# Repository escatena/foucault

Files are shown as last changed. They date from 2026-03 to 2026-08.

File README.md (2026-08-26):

# 📺 Watch the video

Watch on YouTube (https://www.youtube.com/watch?v=r8lBbuhs2y4)
Watch on YouTube (https://www.youtube.com/watch?v=cCXCGMFah08)

---

# 📌 Abstract
**A short driven Foucault pendulum at 26.9°S latitude**

In this paper it is discussed the construction of a short Foucault pendulum (2.4 meters long, compared to the several dozen meters typically found in museums and science centers). The pendulum is driven by a standard electromagnet and suspended using a small pin vise. A magnetic sensor is placed directly beneath the pendulum’s equilibrium point to track its motion, enabled by a small neodymium magnet attached to the bottom of the bob. The sensor is connected to an Arduino UNO board (ATmega328P), which processes the readings to control the electromagnet that provides controlled impulses to the pendulum, while also tracking the precession angle of the pendulum’s oscillation plane. This method eliminates the need for a secondary detection coil, commonly employed in similar setups, thereby simplifying the electronic circuit compared with other implementations. Using this approach, it was found a precession rate of 6.8 ± 0.3 °/h, in agreement with the expected theoretical prediction for our latitude.

The full paper describing the experiment can be fount at https://www.scielo.br/j/rbef/a/hsv8dhmVLGM85JyyM8W3H9k/?lang=en&ilang=pt_BR

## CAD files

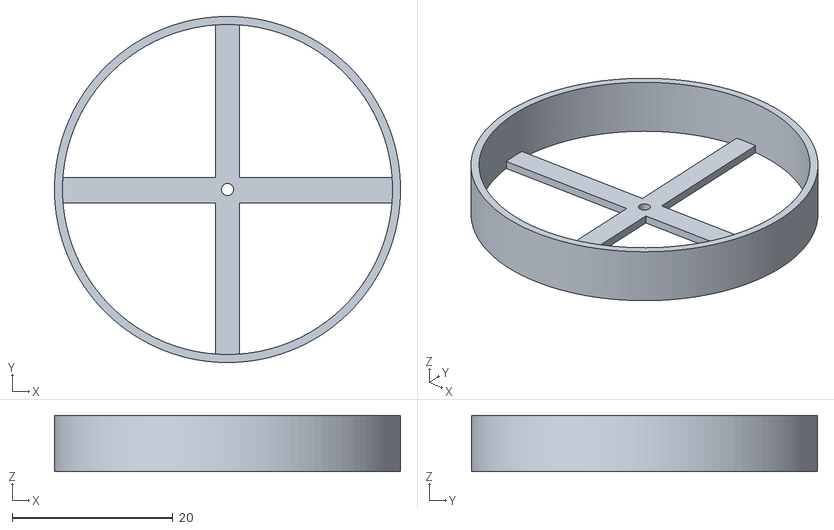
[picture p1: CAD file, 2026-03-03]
3D printed parts/Aligment tool/target.stl
43.0 x 43.0 x 7.00

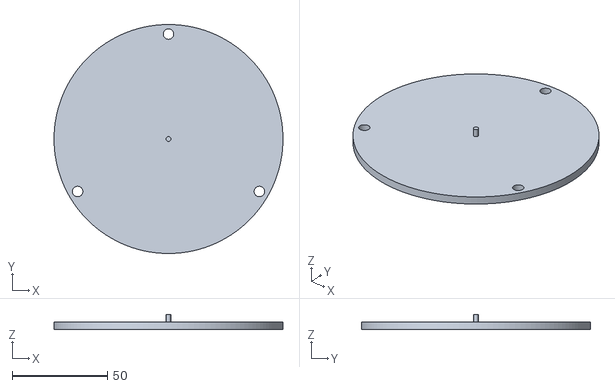
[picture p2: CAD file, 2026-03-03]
3D printed parts/Base/sensor support.stl
120.0 x 120.0 x 8.00

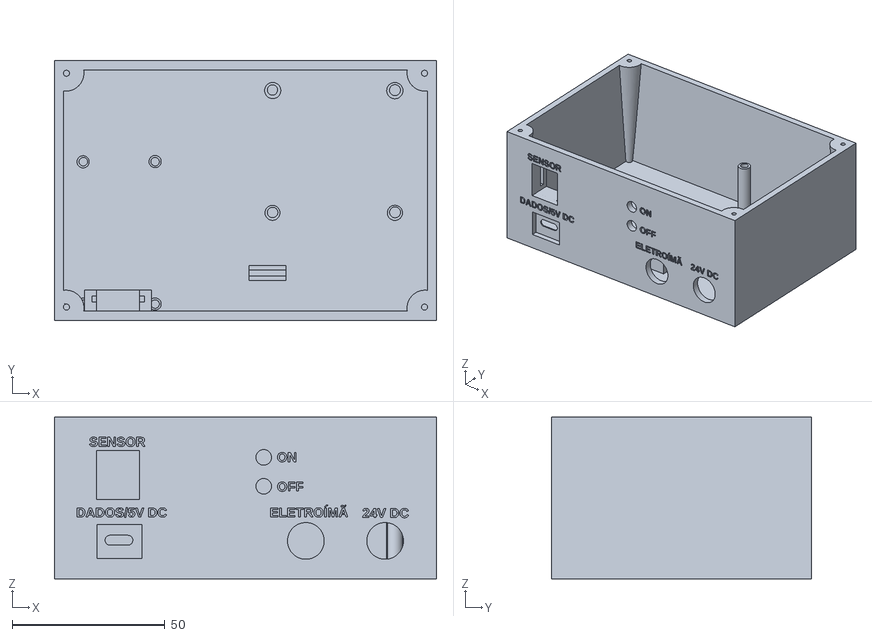
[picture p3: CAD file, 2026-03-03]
3D printed parts/Case eletronics/case-esp32.stl
125.0 x 85.0 x 53.0

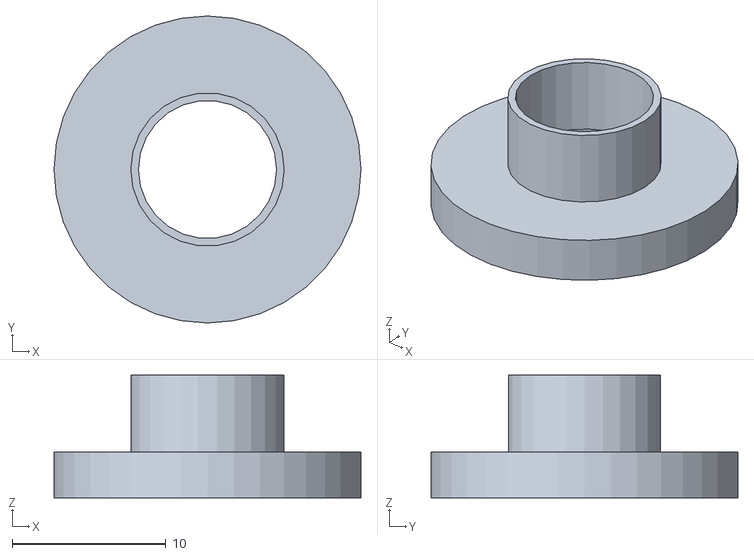
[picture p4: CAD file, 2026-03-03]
3D printed parts/Charron adapter/adaptador-charon-09.stl
20.0 x 20.0 x 8.00

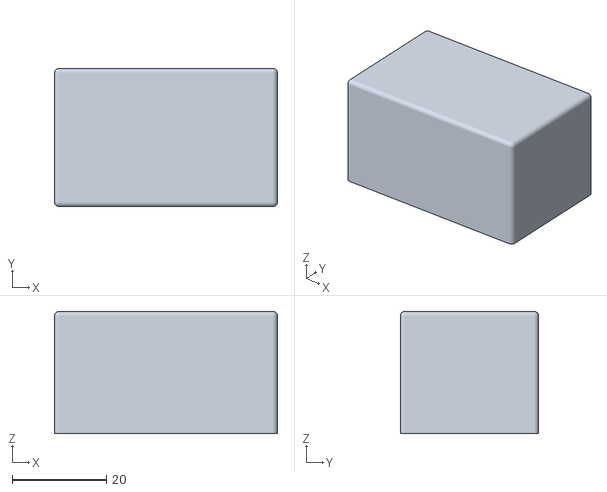
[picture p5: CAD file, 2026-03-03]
3D printed parts/Sensor case/case-sensor-lid.stl
47.4 x 29.4 x 26.0

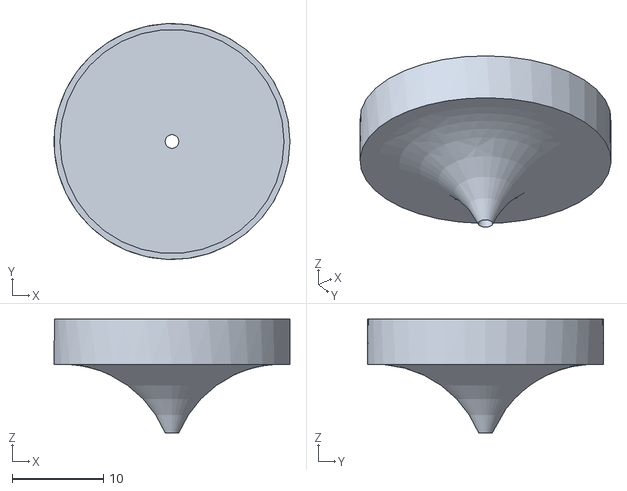
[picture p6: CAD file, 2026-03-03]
3D printed parts/Aligment tool/pointer.stl
25.9 x 25.9 x 12.5

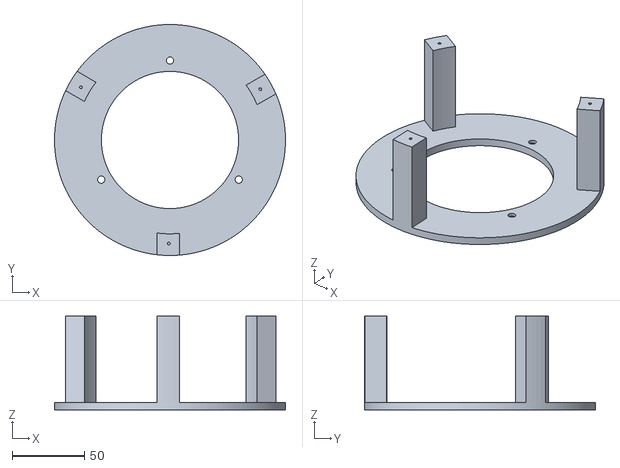
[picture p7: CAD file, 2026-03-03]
3D printed parts/Base/base.stl
160.0 x 160.0 x 65.0

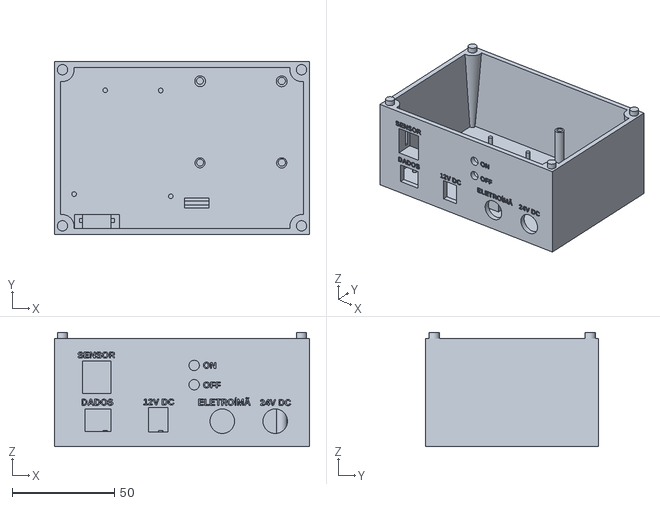
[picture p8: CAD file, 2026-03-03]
3D printed parts/Case eletronics/case-arduino.stl
125.0 x 85.0 x 56.0

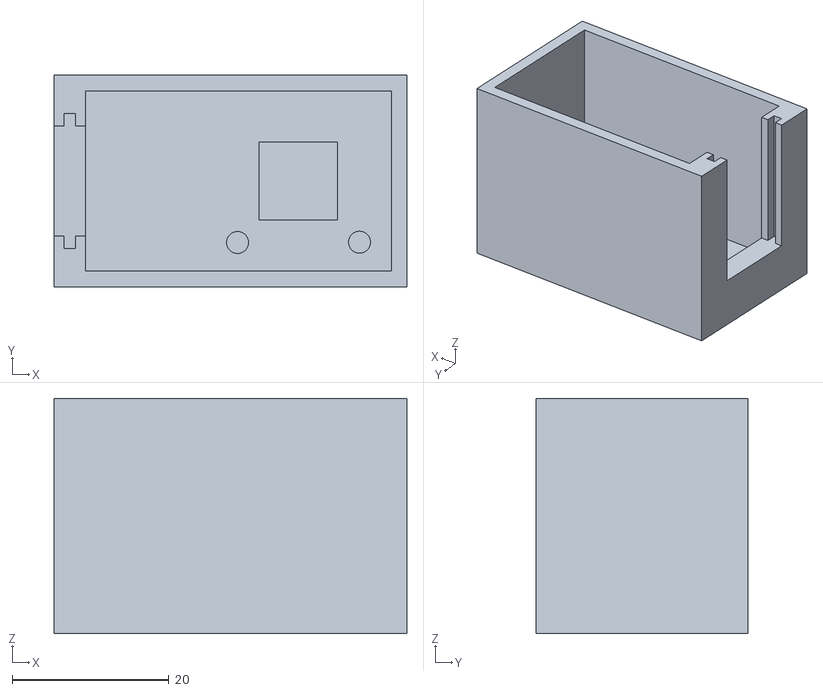
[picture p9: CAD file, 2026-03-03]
3D printed parts/Sensor case/case-sensor.stl
45.0 x 27.0 x 30.0

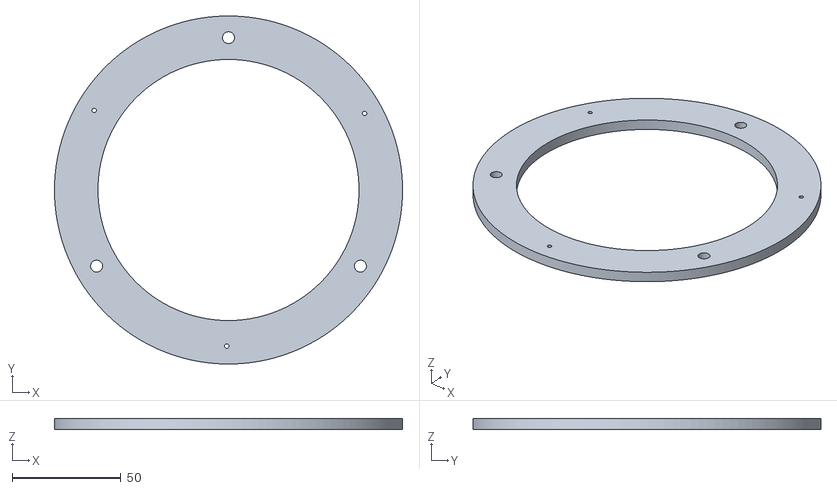
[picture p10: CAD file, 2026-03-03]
3D printed parts/Base/platform.stl
160.0 x 160.0 x 5.00

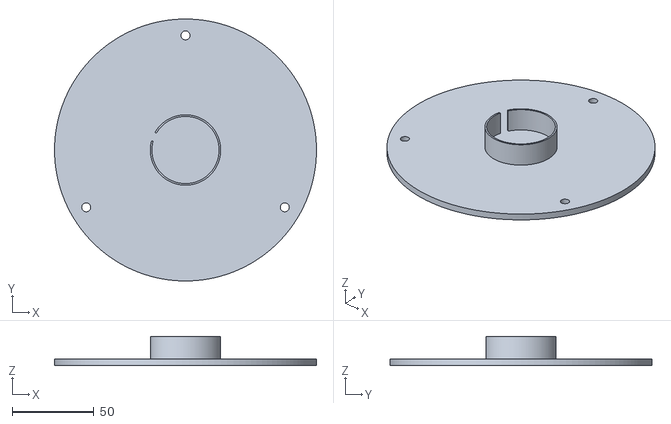
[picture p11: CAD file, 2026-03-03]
3D printed parts/Base/electromagnet support.stl
160.0 x 160.0 x 18.0

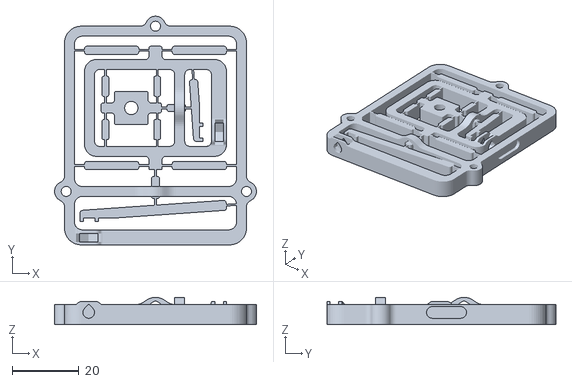
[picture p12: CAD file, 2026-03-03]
3D printed parts/Base/compliant mechanism.stl
60.5 x 68.5 x 8.22

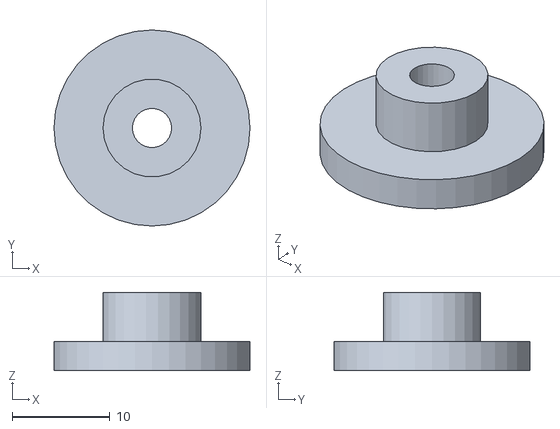
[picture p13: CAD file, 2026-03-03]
3D printed parts/Charron adapter/adaptador-charon-04.stl
20.0 x 20.0 x 8.00

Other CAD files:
3D printed parts/Charron adapter/adaptador-charon-07.stl
3D printed parts/Charron adapter/adaptador-charon-05.stl
3D printed parts/Charron adapter/center-charon.stl
3D printed parts/Charron adapter/adaptador-charon-06.stl
3D printed parts/Charron adapter/adaptador-charon-08.stl

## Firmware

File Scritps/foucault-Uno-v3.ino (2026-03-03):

#include <QMC5883LCompass.h>
#include <math.h>

QMC5883LCompass compass;

// =====================================================
// ================= PINS ==============================
// =====================================================

#define RIGHT_PWM 5
#define LEFT_PWM 4
#define RIGHT_ENABLE 3
#define LEFT_ENABLE 2
#define LED_MEASURE 8
#define LED_COIL 9

// =====================================================
// ================= STATES ============================
// =====================================================

enum ElectromagnetState { OFF, PULL, PUSH };
ElectromagnetState electromagnetState = OFF;

enum SystemState {
  CYCLE_IDLE,
  CYCLE_ACTIVE
};

SystemState systemState = CYCLE_IDLE;

// =====================================================
// ================= TIMING ============================
// =====================================================

unsigned long peakTime = 0;
unsigned long timeBetweenPeaks = 0;

unsigned long pushStartTime = 0;
unsigned long pullStartTime = 0;
unsigned long electromagnetOffTime = 0;

const unsigned long pushDelay = 50;
const unsigned long pushDuration = 200;

const unsigned long pullDelay = 100;
const unsigned long pullDuration = 100;

const unsigned long measurementDelay = 350;

const unsigned long minimumTimeBetweenPeaks = 1000;
const double peakTolerance = 2;

// =====================================================
// ================= SENSOR ============================
// =====================================================

double xValue, yValue, zValue;
double xOffset = 0;
double yOffset = 0;
double zOffset = 0;

bool measurementReady = false;
bool measurementDone = false;
bool offWindowActive = false;

double deltaX[2];
double deltaY[2];
int angleSampleCount = 0;
double angle;
double angleTime;

// =====================================================
// ===================== SETUP =========================
// =====================================================

void setup() {

  Serial.begin(19200);

  compass.init();
  compass.setSmoothing(10, true);
  compass.setCalibrationScales(0.1, 0.1, 0.1);

  pinMode(RIGHT_PWM, OUTPUT);
  pinMode(LEFT_PWM, OUTPUT);
  pinMode(LEFT_ENABLE, OUTPUT);
  pinMode(RIGHT_ENABLE, OUTPUT);
  pinMode(LED_COIL, OUTPUT);
  pinMode(LED_MEASURE, OUTPUT);

  digitalWrite(LEFT_ENABLE, HIGH);
  digitalWrite(RIGHT_ENABLE, HIGH);

  delay(1000);
}

// =====================================================
// ===================== LOOP ==========================
// =====================================================

void loop() {

  digitalWrite(LED_MEASURE, LOW);

  unsigned long now = millis();

  updateSensor();
  updateControl(now);
  updateMeasurement(now);

  sendSerialData();

  measurementDone = false;
}

// =====================================================
// ================= CONTROL ===========================
// =====================================================

void updateControl(unsigned long now) {

  if (detectPeak(zValue)) {

    timeBetweenPeaks = now - peakTime;
    peakTime = now;

    pushStartTime = now + pushDelay;
    pullStartTime = now + timeBetweenPeaks / 2 + pullDelay;

    systemState = CYCLE_ACTIVE;
  }

  if (systemState != CYCLE_ACTIVE)
    return;

  // ===== PUSH WINDOW =====
  if (now >= pushStartTime &&
      now <= pushStartTime + pushDuration) {

    controlElectromagnet(OFF);   // Change to PUSH to actively push
  }

  // ===== PULL WINDOW =====
  else if (now >= pullStartTime &&
           now <= pullStartTime + pullDuration) {

    controlElectromagnet(PULL);
  }

  // ===== MEASUREMENT WINDOW =====
  else if (now >= pushStartTime + pushDuration &&
           now < pullStartTime) {

    controlElectromagnet(OFF);

    if (!offWindowActive) {
      electromagnetOffTime = now;
      offWindowActive = true;
    }
  }

  // ===== END OF CYCLE =====
  else if (now > pullStartTime + pullDuration) {

    controlElectromagnet(OFF);
    offWindowActive = false;
    measurementReady = false;
    systemState = CYCLE_IDLE;
  }
}

// =====================================================
// ================= MEASUREMENT =======================
// =====================================================

void updateMeasurement(unsigned long now) {

  if (!offWindowActive) return;
  if (electromagnetState != OFF) return;
  if (now <= electromagnetOffTime + measurementDelay) return;
  if (measurementReady) return;

  digitalWrite(LED_MEASURE, HIGH);

  measurementReady = true;
  measurementDone = true;

  calculateAngle(angleTime, angle);
}

// =====================================================
// ================= PEAK DETECTION ====================
// =====================================================

bool detectPeak(double currentValue) {

  static double previousValue = 0;
  static bool rising = false;

  if (abs(currentValue - previousValue) > peakTolerance) {

    if (currentValue > previousValue)
      rising = true;

    else if (rising && currentValue < previousValue) {

      rising = false;

      if (millis() - peakTime > minimumTimeBetweenPeaks) {
        previousValue = currentValue;
        return true;
      }
    }
  }

  previousValue = currentValue;
  return false;
}

// =====================================================
// ============ ELECTROMAGNET CONTROL ==================
// =====================================================

void controlElectromagnet(ElectromagnetState state) {

  electromagnetState = state;

  switch (state) {

    case OFF:
      digitalWrite(RIGHT_PWM, LOW);
      digitalWrite(LEFT_PWM, LOW);
      digitalWrite(LED_COIL, LOW);
      break;

    case PULL:
      digitalWrite(RIGHT_PWM, LOW);
      digitalWrite(LEFT_PWM, HIGH);
      digitalWrite(LED_COIL, HIGH);
      break;

    case PUSH:
      digitalWrite(RIGHT_PWM, HIGH);
      digitalWrite(LEFT_PWM, LOW);
      digitalWrite(LED_COIL, HIGH);
      break;
  }
}

// =====================================================
// ================= SENSOR UPDATE =====================
// =====================================================

void updateSensor() {
  compass.read();
  xValue = compass.getX() + xOffset;
  yValue = compass.getY() + yOffset;
  zValue = compass.getZ() + zOffset;
}

// =====================================================
// ================= ANGLE =============================
// =====================================================

void calculateAngle(double &timeAngle, double &computedAngle) {

  deltaX[angleSampleCount] = xValue;
  deltaY[angleSampleCount] = yValue;
  angleSampleCount++;

  if (angleSampleCount < 2) return;

  angleSampleCount = 0;

  if (deltaX[1] == deltaX[0]) return;

  computedAngle = atan((deltaY[1] - deltaY[0]) /
                       (deltaX[1] - deltaX[0])) * 180.0 / PI;

  if (computedAngle < 0)
    computedAngle += 180;

  timeAngle = millis();
}

// =====================================================
// ================= SERIAL OUTPUT =====================
// =====================================================

void sendSerialData() {

  Serial.print(millis());
  Serial.print(" ; ");
  Serial.print(xValue);
  Serial.print(" ; ");
  Serial.print(yValue);
  Serial.print(" ; ");
  Serial.print(zValue);
  Serial.print(" ; ");
  Serial.print(angleTime);
  Serial.print(" ; ");
  Serial.print(angle);
  Serial.print(" ; ");
  Serial.println(measurementDone);
}

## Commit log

2026-03-03 Rename DadosAjustados-22-03-25.csv to first run -22-03-25.csv
    [first run -22-03-25.csv]
2026-03-08 Create High-precision Compliant XY-Positioning Device
